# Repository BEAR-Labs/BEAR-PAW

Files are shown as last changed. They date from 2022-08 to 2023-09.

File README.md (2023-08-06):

# BEAR-PAW
                                                                                                                                                                      

Contact Information:

Email: ucdbearlabs@gmail.com

The Bionic Engineering and Assistive Robotics Pediatric Assistive Ware (BEAR PAW) is a dexterous pediatric prosthetic hand sized for the 8-year-old population and capable of multiple hand grasp configurations. The BEAR PAW has 6 degrees of actuation (individual digit flexion and thumb palmar abduction) and is an underactuated hand with 11 degrees of freedom. The figure below give a general overview of the BEAR PAW.

BEAR PAW

# License

The hardware of the BEAR PAW is released under the Creative Commons BY-SA 4.0 license. The software of the BEAR PAW is released under the GNU General Public License v3. Both licenses have local copies available in the repository under the hardware and software folders.

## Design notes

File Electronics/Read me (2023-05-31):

This is a zipped file for the PCB breakout board. Download the zipped file and then upload the zipped file to osh park (a pcb fabrication company). Use the link below.

https://oshpark.com/

Minimum order of 3 boards is required, this is perfect as you will need 1 for each hand (and an extra for potential mistakes). Should cost around $4.50 for all three.

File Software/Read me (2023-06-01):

To upload the adruino code to the Arduino Pro Mini you will need to use the FTDI USB to TTL converter. This will require that you download the FTDI drivers. Link can be found below. 

https://ftdichip.com/drivers/d2xx-drivers/

The driver version used was the 2.12.28 but this is no longer supported. It can be found at the link above but newer version should still work.

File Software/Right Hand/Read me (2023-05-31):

This is the arduino code for the right hand BEAR PAW.

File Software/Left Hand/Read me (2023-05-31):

This is the arduino code for the left hand BEAR PAW.

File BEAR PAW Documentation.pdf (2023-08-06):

### Contributors: Marcus Battraw, Martin Croshaw, Pranav Tirumalai

### Date: 8-05-23

# BEAR PAW

## Assembly Manual

## Contents

1. Introduction | 2
2. Nomenclature | 2
2.1 Digits & Joints | 2
2.2 Naming Convention for 3D Printed Parts | 3
3. Required Materials | 4
3.1 3D Printed Parts | 4
3.1.1 Table 1: Parts for 3D Printing | 4
3.2 Ordered Parts | 5
3.3 Tools | 8
4. Assembly Flowchart | 7
5. Fingers (D2|5) | 7
5.1 Preparations | 7
5.1.1 Sanding Parts in Order to Ensure Proper Fit | 7
5.1.2 Fingertip Mold | 8
5.1.3 Proximal Part (D2|5) | 8
5.1.4 Distal Part | 9
5.2 Assembly | 11
6. Thumb (D1) | 12
6.1 Preparations | 12
6.1.1 Sanding Parts in Order to Ensure Proper Fit | 12
6.1.2 Thumb-tip Mold | 13
6.1.3 Proximal Part | 13
6.1.4 Distal Part | 13
6.2 Assembly | 15
7. Palm | 17
7.1 Preparations | 17
8.2 Mount the Digits D1|5 to the Palm | 19
7.3 Motor Placement | 20
7.3.1 Wire Cutting | 20
7.4. Mounting Tendons and Motors | 22
7.4.1 Fingers - D2|5 | 22
7.4.2 Thumb - D1 | 23
7.5 Covers and Wrist | 24
8. Hardware and Software | 26
8.1 Soldering | 26
8.2 Wiring | 28
8.2 Programming | 30

## 1. Introduction

While pediatric prosthetic devices are emerging on clinical and experimental horizons, researchers are missing a well-validated, robust device with open access to hardware and software. The straightforward and inexpensive Pediatric Assistive Ware designed at the UC Davis Bionic Engineering and Assistive Robotics Lab (BEAR PAW) provides an open-source platform to bridge this gap in knowledge. Dexterous, multiarticulate, and versatile in hand grasping patterns, the BEAR PAW will provide a platform for studies to improve understanding of how children will control prostheses. Ultimately, enabling such studies will improve the translation of dexterous multi-grasp prosthetic devices to the pediatric population. Complete with materials, definitions, and pictorial instructions, this guide allows any interested individual or team to create the BEAR PAW.

## 2. Nomenclature

### 2.1 Digits & Joints

Naming convention: Digit-Position/Joint
i.e. D3-JI (Digit 3 – Intermediate Joint) or D2-DI (Digit 2 – Distal and Intermediate)
Note that “I” is for Intermediate (i.e., the joint or phalanx in the middle of the finger, but since we couple the intermediate and distal components it is also the most distal component) and “P” for proximal (i.e., the joint or phalanx attaching the finger to the palm). The ability to rotate 90° into the page (assume palm down) is an additional degree of freedom provided to the thumb, and this joint is called out as D1-R.

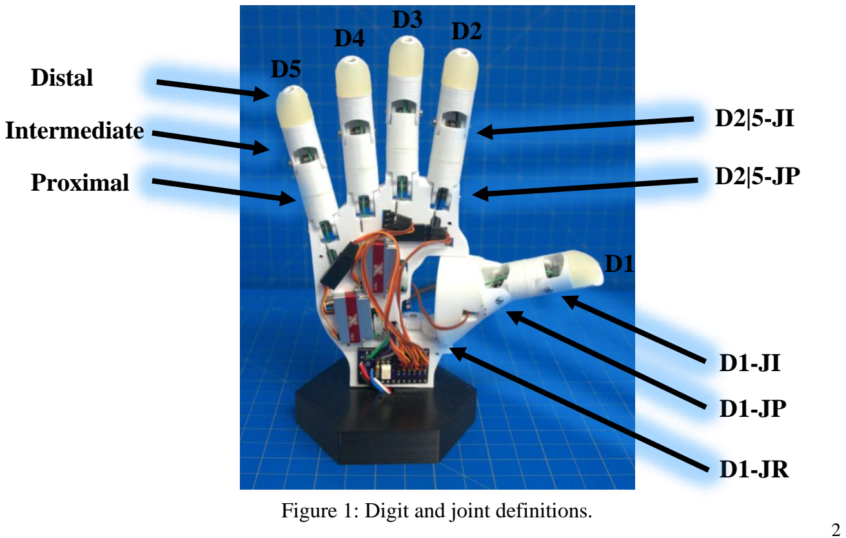
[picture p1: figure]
Figure 1: Digit and joint definitions.; Distal; Intermediate; Proximal

NOTE: The distal joint in a child’s hand poses a manufacturing obstacle due to its small nature. Additionally, it has a negligible range of motion. Thus, this design includes only two joints in each finger: the intermediate and proximal, with the distal and intermediate phalanges connected as a single part.

### 2.2 Naming Convention for 3D Printed Parts

3D-Printed Parts Code: Hand-Digit(s)/Palm-Part

Hand: Right (R), Left (L)

Digit(s): D1-D5. Since the parts and assemblies of D2, D3, D4 & D5 are identical, these are collectively called out as D2|5.

Palm: Surface of the hand.

Part: The parts for each of the above designations.

- Digit Parts: D2-D5
- Distal: (DPhal)
- Intermediate: (IPhal)
- Proximal: Comes in two parts, a distal and proximal part, for ease of printing.
- Distal-most part of proximal: (PPhal-DPart)
- Proximal-most part of proximal: (PPhal-PPart)
- Tendon tightening mount: (Tensioner)
- Negative of fingertip: Comes in two parts for easy removal of cured resin.
- (FTNeg1) and (FTNeg2)
- Thumb Parts: D1
- Distal: Comes in two parts—a distal and proximal part, for ease of printing.
- Distal-most part of distal: (DPhal-DPart)
- Proximal-most part of distal: (DPhal-PPart)
- Intermediate: Comes in two parts—a distal and proximal part, for ease of printing.
- Distal-most part of intermediate: (IPhal-DPart)
- Proximal-most part of intermediate: (IPhal-PPart)
- Proximal: Comes in five parts—for ease of printing.
- Distal-most part of proximal: (PPhal-DPart)
- Proximal-most part of proximal: (PPhal-PPart-PalmGear)
- Door, to hide motor in proximal part: (PPhal-PPart-PalmDoor)
- Gear, for motor to mesh with proximal gear for abduction: (PalmGearWheel)
- Tendon tightening mount: (Tensioner)
- Negative of fingertip: Comes in two parts for easy removal of cured resin.
- (FTNeg1) and (FTNeg2)

- Palm Parts
- Main interior frame for motor and digit mounting: (InteriorFrame)
- Front of hand cover: (PalmarCover)
- Back of hand cover: (DorsalCover)

Notes:

- Position/Location: If several parts make up a phalanx, they are referred to by location as being more proximal (closer to the palm) or distal (closer to the fingertip).
- Fingertip (FT) mold only needs to be printed once and can be reused.

## 3. Required Materials

### 3.1 3D Printed Parts

General printer settings used.

Printer | SigmaxR19
Hotend Nozzle | 0.4 mm
Material | PLA
Global Layer | 0.15 mm
Infill Density | 25%
Speed | 50 mm/s

3.1.1 Table 1: Parts for 3D Printing
Part Name | Unique Print Settings | Print Length (meters) | Approximate Print Time | Part Mass
R/L-D2|5-PPhal-PPart X 4 | None | 0.23 m X 4 = 0.92 m | 26 min X 4 = 1 hr 44 min | 2 g X 4 = 8 g
R/L-D2|5-PPhal-DPart X 4 | None | 0.21 m X 4 = 0.84 m | 24 min X 4 = 1 hr 36 min | 2 g X 4 = 8 g
R/L-D2|5-IPhal X 4 | None | 0.22 m X 4 = 0.88 m | 26 min X 4 = 1 hr 44 min | 2 g X 4 = 8 g
R/L-D2|5-DPhal X 4 | None | 0.12 m X 4 = 0.48 m | 13 min X 4 = 52 min | 1 g X 4 = 4 g
R/L-D2|5-Tensioner X 4 | None | 0.02 m X 4 = 0.08 m | 3 min X 4 = 12 min | ~ 0 g
R/L-D2|5-FTNeg1 | None | 1.00 m | 1 hr 16 min | 8 g
R/L-D2|5-FTNeg2 | None | 0.72 m | 51 min | 6 g
R/L-D1-PPhal-PPart-PalmGear | Infill 50% Global; 0.1 mm; Using Supports Advisable | 1.33 m | 2 hrs 50 min | 11 g
R/L-D1-PPhal-PPart-PalmDoor | None | 0.34m | 34 min | 3g
R/L-D1-PPhal-DPart | None | 0.29m | 28 min | 2 g

R/L-D1-IPhal-PPart | None | 0.24 m | 25 min | 2 g
R/L-D1-IPhal-DPart | None | 0.21 m | 20 min | 2 g
R/L-D1-DPhal-PPart | None | 0.15 m | 20 min | 1 g
R/L-D1-DPhal-DPart | None | 0.15 m | 15 min | 1 g
R/L-D1-PalmGearWheel | None | 0.08 m | 11 min | 1 g
R/L-D1-Tensioner | None | 0.02 m | 3 min | ~ 0 g
R/L-D1-FTNeg1 | None | 0.98 m | 1 hr 17 min | 8 g
R/L-D1-FTNeg2 | None | 0.72 m | 53 min | 6 g
R/L-Palm-DorsalCover | Infill 35% Global; 0.12 mm; Use Supports | 2.63 m | 4 hrs 53 min | 21 g
R/L-Palm-InteriorFrame | Infill 35% Global; 0.1 mm; Use Supports | 2.75 m | 6 hrs 39 min | 22 g
R/L-Palm-PalmarCover | 0.12 mm; Use Supports | 1.67 m | 3 hrs 10 min | 13 g
R/L-Wrist-BaseMount | None | 2.56 m | 3 hrs 27 min | 20 g
R/L-Wrist-HandAdapter | None | 1.22 m | 1 hr 44 min | 10 g
R/L-Wrist-HandMount | None | 1.02 m | 1 hr 27 min | 8 g
| Totals: | 21.28 m | 37 hrs 11 min | 173 g
NOTE: Supports advised when there is an extensive hole or overhanging arch; alternatively, consider printing in a different orientation.

NOTE: X 4 on the finger part values to account for all fingers D2|5.

NOTE: Printed several parts in 1 G-code file to speed up the process.

### 3.2 Ordered Parts

Table 2 below contains all the necessary items to build a complete BEAR PAW. This table was finalized on 8/25/2022; therefore, some items may be discontinued, or cost of items may have changed. The cost shown does not account for shipping/tax or any additional costs that may be incurred.

Table 2: Parts for Ordering

Item | Description | Vendor | Part
No.
Link | Qty. | Cost/Item | Ext.
Cost
SENSORS/ELECTRONICS
KST X08N V5.0 | Micro Servo Motor with no mounting flanges | Alofthobbies | X08N | https://alofthobbies.com/k st-x08n.html (https://alofthobbies.com/kst-x08n.html) | 1 | $46.00 | $46.00
KST X08H V5.0 | Micro Servo Motor with top mounting flanges | Alofthobbies | X08H | https://alofthobbies.com/k st-x08h-servo-2-8kg-38-oz-in-09-sec-8-grams-wide-voltage.html (https://alofthobbies.com/kst-x08h-servo-2-8kg-38-oz-in-09-sec-8-grams-wide-voltage.html) | 1 | $46.00 | $46.00
KST X08 V5.0 | Micro Servo Motor with side mounting flanges | Alofthobbies | X08 | https://alofthobbies.com/k st-x08-servo-2-8kg-38-oz-in-09-sec-8-grams.html (https://alofthobbies.com/kst-x08-servo-2-8kg-38-oz-in-09-sec-8-grams.html) | 4 | $46.00 | $184.00
Breakout Board | 2 layer electronics breakout board, 17.8 x 33.0mm | OSHPARK | Find Gerber files on GitHub | https://docs.oshpark.com/services/two-layer/ (https://docs.oshpark.com/services/two-layer/) | 1 | $5.00 | $5.00
Solid State Relay | Omron, Solid State Relay - PCB Mount, 3 A, 60 V | Mouser Electronics | 653-G3VM-61AR1 | https://www.mouser.com/ProductDetail/Omron-Electronics/G3VM-61AR1?qs=wnTfsH77Xs7 4FCx6Uqk9GQ%3D%3D (https://www.mouser.com/ProductDetail/Omron-Electronics/G3VM-61AR1?qs=wnTfsH77Xs74FCx6Uqk9GQ%3D%3D) | 1 | $6.91 | $6.91
Resistor | 5,600 Ohm Resistor, 5%, 0.5W Through Hole Resistor | DigiKey | S5.6KH CT-ND | https://www.digikey.com/en/products/detail/stackpol e-electronics-inc/CFM12JT5K60/17419 74?s=N4IgTCBcDaIMID ECyBGMApAKgVgNID YAGEAXQF8g (https://www.digikey.com/en/products/detail/stackpole-electronics-inc/CFM12JT5K60/1741974?s=N4IgTCBcDaIMIDECyBGMApAKgVgNIDYAGEAXQF8g) | 1 | $0.10 | $0.10
Arduino Pro Mini 238 – 3.3V/ 8MHz | Micro Controller | Sparkfun | DEV-11114 | https://www.sparkfun.com/products/11114 (https://www.sparkfun.com/products/11114) | 1 | $10.95 | $10.95
FTDI Mini USB to TTL | Mini USB to TTL Adapter Board for Arduino | Amazon | B00IJXZ Q7C | https://www.amazon.com/HiLetgo-FT232RL-Converter-Adapter-Breakout/dp/B00IJXZQ7C/ (https://www.amazon.com/HiLetgo-FT232RL-Converter-Adapter-Breakout/dp/B00IJXZQ7C/) | 1 | $6.99 | $6.99
Bluetooth Module | DSD Tech HC-05 Bluetooth Serial Module | Amazon | B01G9K SAF6 | https://www.amazon.com/DSD-TECH-HC-05-Pass-through-Communication/dp/B01G9KSAF6/ (https://www.amazon.com/DSD-TECH-HC-05-Pass-through-Communication/dp/B01G9KSAF6/) | 1 | $9.99 | $9.99
Power Wires | 22 Gauge Silicone wire spool red 25ft and black 25ft | Amazon | B07HGT 44XY | https://www.amazon.com/BNTECHGO-Silicone-Flexible-Strands- (https://www.amazon.com/BNTECHGO-Silicone-Flexible-Strands-Stranded/dp/B07HGT44XY/?th=1) | 1 | $9.98 | $9.98

| | | | Stranded/dp/B07HGT44X Y/?th=1 (https://www.amazon.com/BNTECHGO-Silicone-Flexible-Strands-Stranded/dp/B07HGT44XY/?th=1)
Extra Servo Wires | 30 Gauge Silicone Wire Kit | Amazon | B01M70 EDCW | https://www.amazon.com/dp/B01M70EDCW?th=1 (https://www.amazon.com/dp/B01M70EDCW?th=1) | 1 | $9.98 | $9.98
Connecto r Kit | 2.54 mm Crimp Pin Connector Housings, Single Row Male Headers, Male/Female Crimp Pins and Ribbon Cable | Amazon | B078RR PRQZ | https://www.amazon.com/Dupont-Connector-Kit-Connectors-Plusivo/dp/B078RRPRQZ/ (https://www.amazon.com/Dupont-Connector-Kit-Connectors-Plusivo/dp/B078RRPRQZ/) | 1 | $12.99 | $12.99
Wall Adapter | AC/DC Wall Mount Adapter 5V, 20W | DigiKey | 102-4196-ND | https://www.digikey.ca/en/products/detail/cui-inc/SWI25-5-N-P5/7070092 (https://www.digikey.ca/en/products/detail/cui-inc/SWI25-5-N-P5/7070092) | 2 | $27.89 | $55.78
Wall Jack | DC Barrel Jack Adapter - Female | Sparkfun | 10288 | https://www.sparkfun.com/products/10288 (https://www.sparkfun.com/products/10288) | 2 | $3.50 | $7.00
CENTAU RUS Servo Tester STV2.3 | Steering Gear Rudder Detector Spare Parts for RC Aircraft Micro FPV DC 4.8V-6V | Amazon | B09LXT W19G | https://www.amazon.com/CENTAURUS-Steering-Detector-Aircraft-4-8V-6V/dp/B09LXTW19G (https://www.amazon.com/CENTAURUS-Steering-Detector-Aircraft-4-8V-6V/dp/B09LXTW19G) | 1 | $3.50 | $3.50

HARDWARE AND MISCELLANOUS
Bearings | Bearing 2 mm Bore ID, 5 mm OD, 2.5mm | Amazon | B07X9T 5F81 | https://www.amazon.com/Donepart-MR52ZZ-Bearings-Miniature-Equipment/dp/B07X9T5F 81 (https://www.amazon.com/Donepart-MR52ZZ-Bearings-Miniature-Equipment/dp/B07X9T5F81) | 1 | $9.99 | $9.99
Pulley for KST X08 Servo | Pulley for KST Servo Pack of 4 | Hyperflight | X08-PULLE Y | https://www.hyperflight.co.uk/products.asp?code=X 08-PULLEY&name=pulley-for-kst-x08-servos-4 (https://www.hyperflight.co.uk/products.asp?code=X08-PULLEY&name=pulley-for-kst-x08-servos-4) | 2 | $11.75 | $23.50
Rotary Shaft 316 Stainless Steel | 2 mm Shaft 200 mm long | McMaster Carr | 1265K17 | https://www.mcmaster.com/1265K17/ (https://www.mcmaster.com/1265K17/) | 1 | $14.27 | $14.27
Torsion Spring | Torsion Spring 180 Degree Right-Hand Wound, 0.186'' OD (Pack of 6) | McMaster Carr | 9271K66 5 | https://www.mcmaster.com/9271K665/ (https://www.mcmaster.com/9271K665/) | 2 | $5.19 | $10.38
Strength Black Synthetic Cable | 0.75mm (0.03") in diameter, 5 m long, 45kg strength | ServoCity | 2908-0075-0005 | https://www.servocity.com/synthetic-cable-black-0-75mm-diameter-5m-length/ (https://www.servocity.com/synthetic-cable-black-0-75mm-diameter-5m-length/) | 1 | $2.99 | $2.99

M2 18-8 Stainless Steel Screw | Narrow Cheese Head Slotted Screws M2 x 0.4mm Thread, 25 mm Long (50 Pack) | McMaster Carr | 91800A0 23 | https://www.mcmaster.com/91800A023/ (https://www.mcmaster.com/91800A023/) | 1 | $10.15 | $10.15
M3 18-8 Stainless Steel Pan Head Screw | M3 x 0.5mm Thread, 8m m Long | McMaster Carr | 92000A1 18 | https://www.mcmaster.com/92000A118/ (https://www.mcmaster.com/92000A118/) | 1 | $5.51 | $5.51
#4 x 1/2" Flat Head Sheet Metal Screws | Screws for attaching the hand onto the wrist mount | Amazon | B08L23 164W | https://www.amazon.com/Sheet-Screws-Phillips-Tapping-Stainless/dp/B08L23164W/ (https://www.amazon.com/Sheet-Screws-Phillips-Tapping-Stainless/dp/B08L23164W/) | 1 | $9.49 | $9.49

Heat Shrink Tubing Kit | Heat Shrink Tubing (650 pcs) | Amazon | B07QM 8249H | https://www.amazon.com/625pcs-Shrink-Tubing-Tubes-Ratio/dp/B07QM8249H/ (https://www.amazon.com/625pcs-Shrink-Tubing-Tubes-Ratio/dp/B07QM8249H/) | 1 | $8.79 | $8.79
Textured Rubber | Multipurpose Neoprene with Crisscross Texture Adhesive-Back Sheet, 12" x 12", 1/32" Thick | McMaster Carr | 8445K61 | https://www.mcmaster.com/8445K61/ (https://www.mcmaster.com/8445K61/) | 1 | $16.67 | $16.67

MATERIALS
Smooth-On Dragon Skin | 10 NV, 2 Pint Set, Trial Unit 2lbs (Moldable material for fingertips) | Reynolds Advanced Materials | MC-1244 | https://www.reynoldsam.com/product/dragon-skin/ (https://www.reynoldsam.com/product/dragon-skin/) | 1 | $35.37 | $35.37
Gorilla Super Glue Gel XL | 25 grams, clear | Amazon | B082XG L21J | https://www.amazon.com/Gorilla-Super-Glue-transparente-102433/dp/B082XGL21J/ (https://www.amazon.com/Gorilla-Super-Glue-transparente-102433/dp/B082XGL21J/) | 1 | $8.88 | $8.88
| | | | | | Total | $571.16

### 3.3 Tools

- SigmaX R19 (3D Printer)
- Crimping Tool

(https://www.amazon.com/dp/B087BGTH1Y)
- Sandpaper / Sanding Tool (Dremel)
- Screwdriver
- Wire Strippers
- Wire Cutter
- Tweezers
- Pliers
- Files
- Soldering Iron & Solder
- Knife
- Heat Gun

## 4. Assembly Flowchart

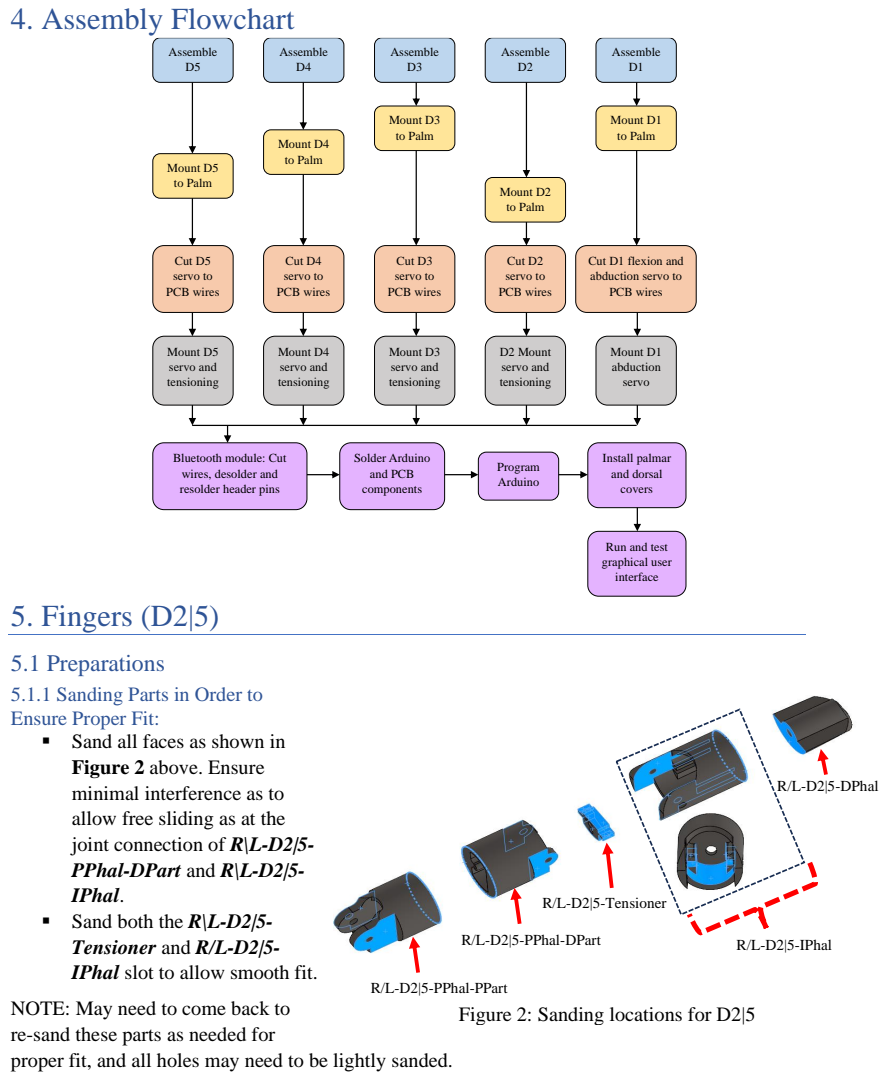
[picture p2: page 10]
5. Fingers (D2|5); R/L-D2|5-PPhal-PPart; R/L-D2|5-PPhal-DPart; R/L-D2|5-Tensioner; R/L-D2|5-IPhal; R/L-D2|5-DPhal; Assemble D5; Assemble D4; Assemble D3; Assemble D2; Assemble D1; Mount D5 to Palm; Mount D4 to Palm; Mount D3 to Palm; Mount D2 to Palm; Mount D1 to Palm; Mount D5 servo and tensioning; Mount D3 servo and tensioning; Mount D4 servo and tensioning; D2 Mount servo and tensioning; Mount D1 abduction servo; Cut D5 servo to PCB wires; Cut D4 servo to PCB wires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

Cut D1 flexion and
abduction servo to
PCB wires

Bluetooth module: Cut
wires, desolder and
resolder header pins

Run and test
graphical user
interface

5.1 Preparations
5.1.1 Sanding Parts in Order to
Ensure Proper Fit:
▪ Sand all faces as shown in
Figure 2 above. Ensure
minimal interference as to
allow free sliding as at the
joint connection of R\L-D2|5-
PPhal-DPart and R\L-D2|5-
IPhal.
▪ Sand both the R\L-D2|5-
Tensioner and R/L-D2|5-
IPhal slot to allow smooth fit.

NOTE: May need to come back to
re-sand these parts as needed for
proper fit, and all holes may need to be lightly sanded.

Figure 2: Sanding locations for D2|5

5.1.2 Fingertip Mold
1. After the R/L-D2|5-FTNeg1 and R/L-D2|5-FTNeg2 are printed, slot together if possible or file to fit in.
2. Then, mix equal parts A and B of the Smooth-On Dragon Skin and pour into the mold. Wait for the recommended time suggested by the Smooth-On instructions.
3. If excess Smooth-On is at the top, cut off evenly with an X-Acto knife.
4. Afterwards, pull apart the mold and repeat the process over again until you have 4 fingertips (Figure 3).

Figure 3: Negative molds for fingertips and thumb

5.1.3 Proximal Part (D2|5)
Orient the two proximal pieces as shown in Figure 4 and glue them.

Proximal torsion spring slots may need to be cleaned so that the spring leg fits in.

This may be difficult even with a small file.

Suggestion: use gloves and a soldering iron. Heat up the spring leg and press the hot leg through the hole to clean it out. Remove before the plastic solidifies.

Rubber

FTNeg
FTNeg
Towards distal end | Distal torsion spring slot

5.1.4 Distal Part
Glue the R/L-D2|5-IPhal to the R/L-D2|5-DPhal; then glue the rubber fingertip on last. See Figures 5a and 5b.

NOTE: It is
convenient to
screw in the
25mm string
tensioner
screw when
gluing these
parts as it
helps keep
everything
aligned.
A. Tendon preparation (D2-5)
1. Prepare the tendon string (synthetic cable) by cutting a 150mm piece. The actual functional length of the string—once completed and assembled—is only about 60mm, but excess allows for error to be corrected. Cut this length of string, careful to do so with as little fraying as possible.
2. Use the M2X25 tensioner screw and screw into the distal part for the string tensioner (Figure 6).
3. The hole for the torsion spring may be difficult to clean even with a small file. Suggestion: use gloves and a soldering iron. Heat up the spring leg and press the hot leg through the hole to clean it out. Remove before the plastic solidifies (Figure 6).
4. Insert the tendon string through to the distal-facing side of the string tensioner and tie a simple knot to secure (knot should be on the side that points towards the fingertip). Remove any excess string.

Figure 5b: Gluing distal surfaces for D2|5

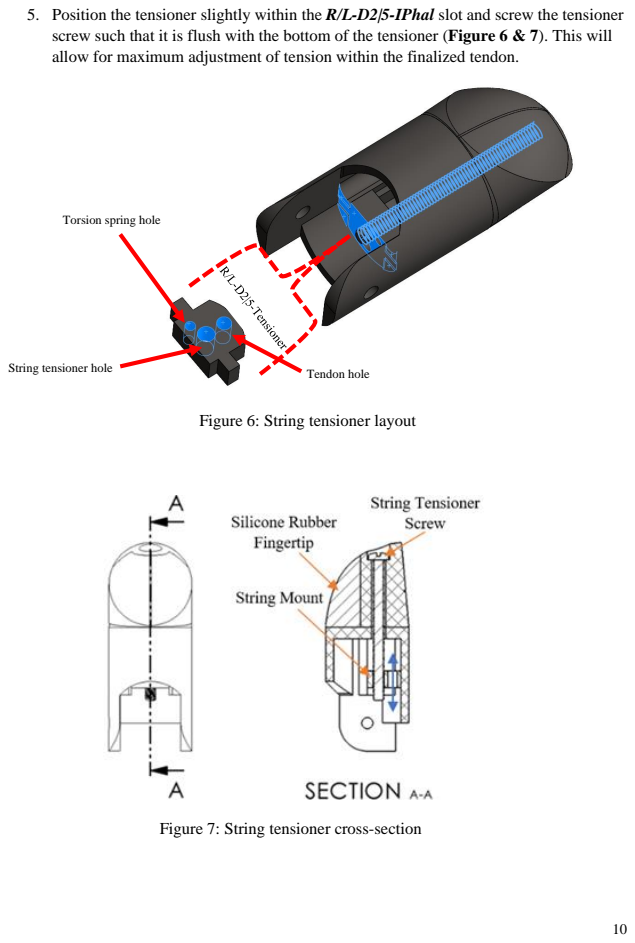
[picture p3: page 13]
Tendon hole

5. Position the tensioner slightly within the R/L-D2|5-IPhal slot and screw the tensioner
screw such that it is flush with the bottom of the tensioner (Figure 6 & 7). This will
allow for maximum adjustment of tension within the finalized tendon.

Torsion spring hole

String tensioner hole

Figure 6: String tensioner layout

Figure 7: String tensioner cross-section

### 5.2 Assembly

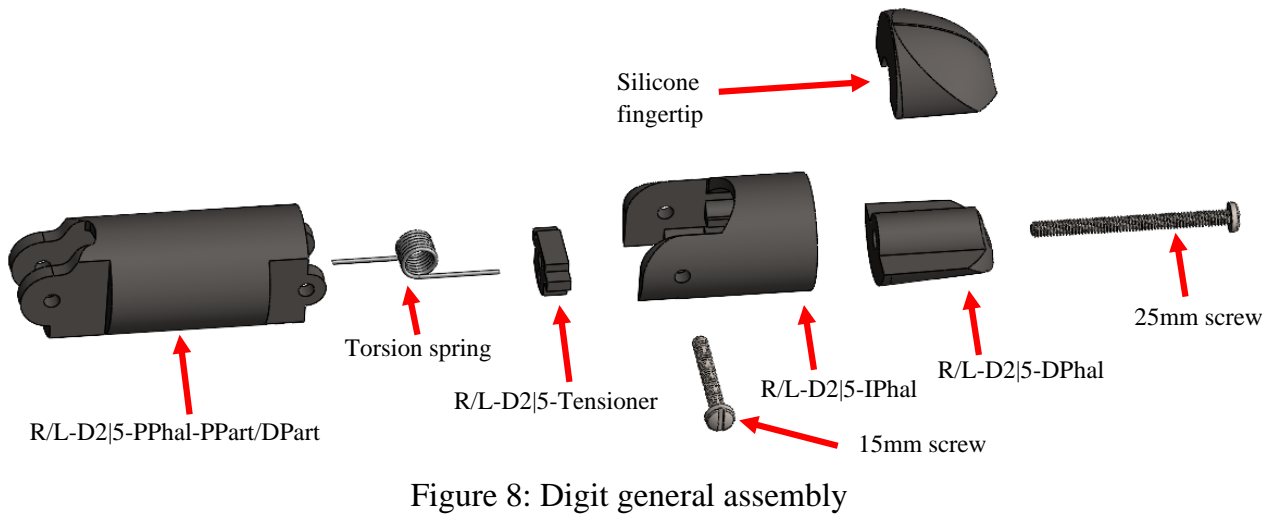
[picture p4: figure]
Figure 8: Digit general assembly; Silicone fingertip; R/L-D2|5-PPhal-PPart/DPart; Torsion spring; R/L-D2|5-Tensioner; R/L-D2|5-IPhal; R/L-D2|5-DPhal; 15mm screw; 25mm screw

1. Cut the screws for joints D2|5-JI and D2|5-JP (15mm). The screw for D2|5-JP will be used later for assembling the digits to the palm.
2. Cut spring legs (they should be approximately 13mm) for joints D2|5-JI.
3. Then with the torsion spring slotted in the torsion spring hole (Figure 6) and the R/L-D2|5-IPhal distal torsion spring slot (Figure 4) join them with the 15mm screw ensuring that the screw goes through the spring and that the tendon is on the palmar side of the digit.

NOTE: Refer to Figure 8 for general layout.

NOTE: Fish the tendon through the palmar side of the finger.

## 6. Thumb (D1)

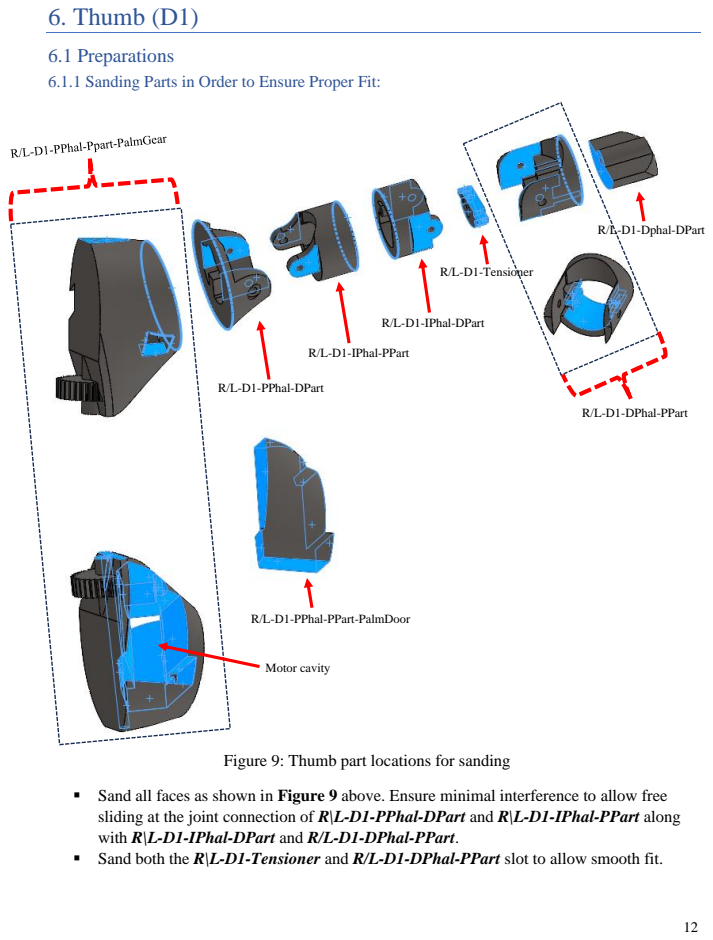
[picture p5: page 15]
R/L-D1-PPhal-DPart; R/L-D1-IPhal-PPart; R/L-D1-IPhal-DPart; R/L-D1-Tensioner; R/L-D1-DPhal-PPart; R/L-D1-Dphal-DPart; Motor cavity

6.1 Preparations
6.1.1 Sanding Parts in Order to Ensure Proper Fit:

R/L-D1-PPhal-PPart-PalmDoor

Figure 9: Thumb part locations for sanding

▪ Sand all faces as shown in Figure 9 above. Ensure minimal interference to allow free
sliding at the joint connection of R\L-D1-PPhal-DPart and R\L-D1-IPhal-PPart along
with R\L-D1-IPhal-DPart and R/L-D1-DPhal-PPart.
▪ Sand both the R\L-D1-Tensioner and R/L-D1-DPhal-PPart slot to allow smooth fit.

- Sand the D1-PPhal-PPart-PalmGear motor cavity so that the servo motor with no flanges fits inside.
- Cut the rod to 57mm. Then, sand the thumb abduction rod to
ensure that it fits into the 2mm inside diameter of the
bearings. This can be done using a hand drill and sandpaper. (See hand drill used in Figure 10 to the right.) Attach the rod as you would a drill bit and pull the trigger while you sand the rod back and forth with the sand paper. Take out the rod
and repeat again on its opposite side. Do this until the rod fits
in the bearing with some resistance.

NOTE: May need to come back to re-sand these parts as needed for proper fit.

6.1.2 Thumb-tip Mold

Refer to Figure 3, Section 5.1.2—similar mold cast for the thumb.

6.1.3 Proximal Part:
1. Ensure the hole on the flat face of the proximal piece goes all the way through to the interior motor cavity (sand if needed), as the tendon string will pass through this hole. The proper hole pathway can be seen in the SolidWorks model provided (Figure 11a).
2. Glue the two parts together in the orientation shown in Figure 11b to the right.

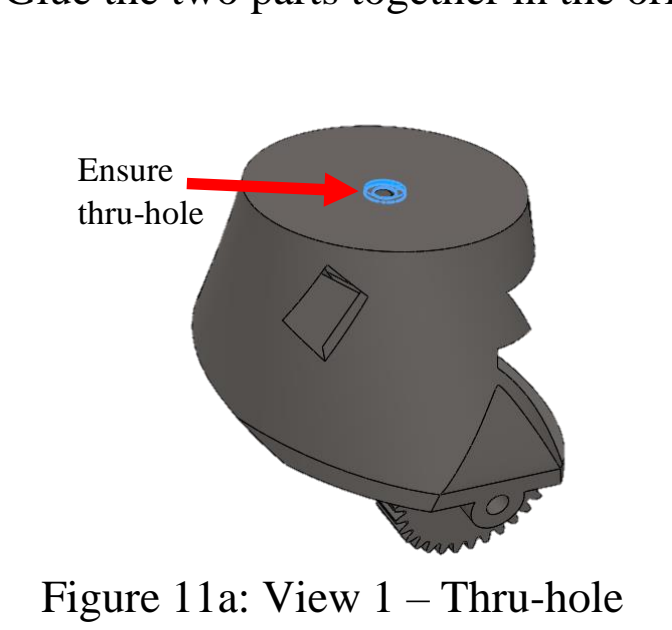
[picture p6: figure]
Figure 11a: View 1 – Thru-hole; Ensure thru-hole

6.1.4 Distal Part:

A. Glue together D1-IPhal-DPart and D1-IPhal-PPart such that the interior slots meant for the torsion springs are on opposite sides as shown in Figure 12. Complete the same process for D1-DPhal-DPart and D1-DPhal-PPart (Figure 13). Additionally, glue the rubber fingertip to the distal part.

Proximal torsion spring slots may need to be cleaned so that the spring leg fits in. This may be difficult even with a small file.

Figure 10: Hand drill used.

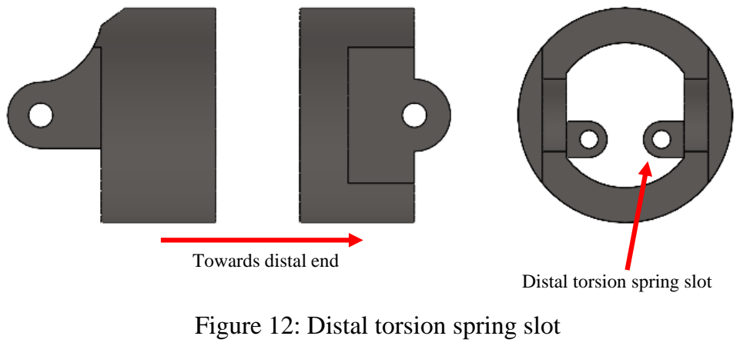
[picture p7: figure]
Distal torsion spring slot; Towards distal end; Figure 12: Distal torsion spring slot

Suggestion: Use gloves and a soldering iron. Heat up the spring leg and press the hot leg through the hole to clean it out. Remove before the plastic solidifies.

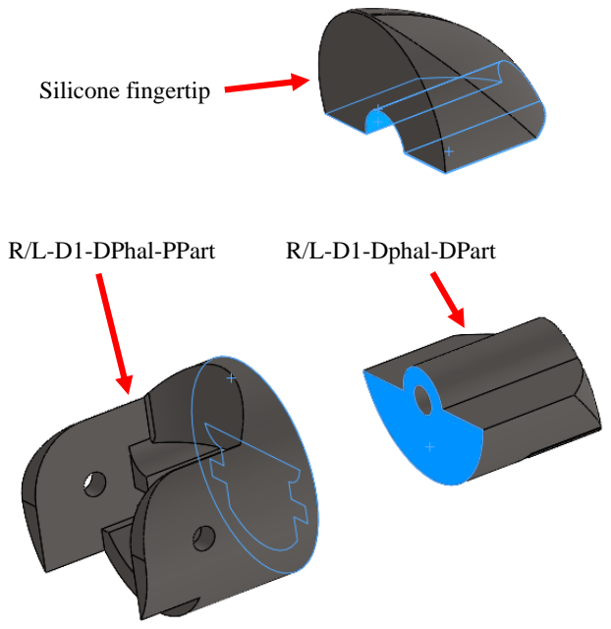
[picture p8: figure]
R/L-D1-DPhal-PPart; R/L-D1-Dphal-DPart; Silicone fingertip

B. Tendon preparation (D2-5)
1. Prepare the tendon string (synthetic cable) by cutting a 150mm piece. The actual functional length of the string once completed and assembled is only about 60mm, but excess allows for error to be corrected. Cut this length of string, careful to do so with as little fraying as possible.
2. Pass the tendon through the D1-PPhal-PPart-PalmGear through-hole as seen in Figure 11a (should be sticking through on both sides).
3. Use the servo motor with no mounting flanges and zero it out with the servo tester (make sure that the zero position is correct such that when the servo is in the thumb it will wind the tendon in the correct direction to flex the thumb). The motor will be installed inside the D1-PPhal-PPart-PalmGear with the pulley side going in first.

Figure 13: Gluing distal surfaces for thumb

4. Using a pointed-nose file, expand the slotting hole (Figure 14) such that the tendon string can pass through with little fraying and resistance. Take care not to completely file away the exterior wall of the slotting hole. Filing of the surrounding features of the pulley may be necessary.
5. Using a lighter or heat gun, burn the 10-15mm of excess string to reduce length, ensuring it sticks to the pulley.
6. Mount the pulley to the servo arm with the servo screw.
7. Place the servo motor inside the D1-PPhal-PPart-PalmGear motor cavity with the pulley side in first. Ensure that the servo wire goes through the slot on the back side.
8. Pull the tendon through the top lightly making sure not to rotate the servo motor. If so, re-zero with the servo tester.

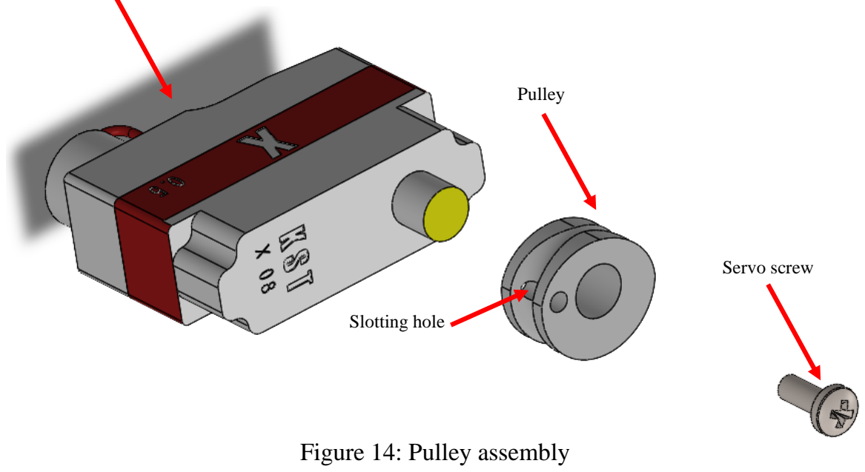
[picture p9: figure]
Pulley; Servo screw; Figure 14: Pulley assembly; Slotting hole

### 6.2 Assembly

1. Cut and file the end of three M2X25 screws; one should be 21mm (proximal joint) D1-JP, the other two should be 18mm (distal joint D1-JI and tensioner screw).
2. At this point, the proximal, intermediate, and distal parts should be completed, along with a string/tendon attached to the installed servo motor and coming out of the thru-hole on part D1-PPhal-PPart-PalmGear.
3. Cut and bend the torsion spring legs so that they fit in the R/L-D1-PPhal-DPart spring slot (90°) and the R/L-D1-IPhal-PPart spring slot. Then use the 21mm screw to attach these two parts while ensuring the screw goes through the center of the torsion spring.
4. Use the 18mm tensioner screw and screw into the now-assembled distal thumb for the string tensioner.

Servo motor

5. Fish the tendon through the glued intermediate part (R/L-D1-IPhal-PPart/DPart) ensuring it is on the palmar side of the spring. Insert the tendon string through to the proximal-facing side of the R/L-D1-Tensioner.
6. (This is the difficult part.) Move the distal thumb assembly of the thumb into position as if you were going to attach it. Observe the length of the tendon needed such that the tensioner can reach the tensioner slot. Remember to provide an extra 2-3mm to the string/tendon as it will have to go over the spring once it is fully assembled. Now tie a simple knot to secure the string/tendon, and place the tensioner in the R/L-D1-DPhal-PPart tensioner slot of the distal thumb assembly. Finally, screw the tensioner screw just enough to grab the tensioner.
7. Now cut the torsion spring legs (approximately 13mm) for D1-JI and place within slots of R/L-D1-IPhal-DPart spring hole and R/L-D1-Tensioner spring hole (remember the tendon should be on the palmar side of the spring). Now join these two parts with the second 18mm screw ensuring it goes through the torsion spring center.
8. Zero out the motor again because it may move during this process. Check to see if the tendon is too loose. You can tighten the tensioner screw, but it may be very loose even after tightening. At this point, you may have to remove the screw at D1-JI and make the string a little shorter (reassemble and try again).
NOTE: This process may take some time, be very careful you don’t rush it or you will remove too much string!

NOTE: Refer to Figure 15 below for general layout.

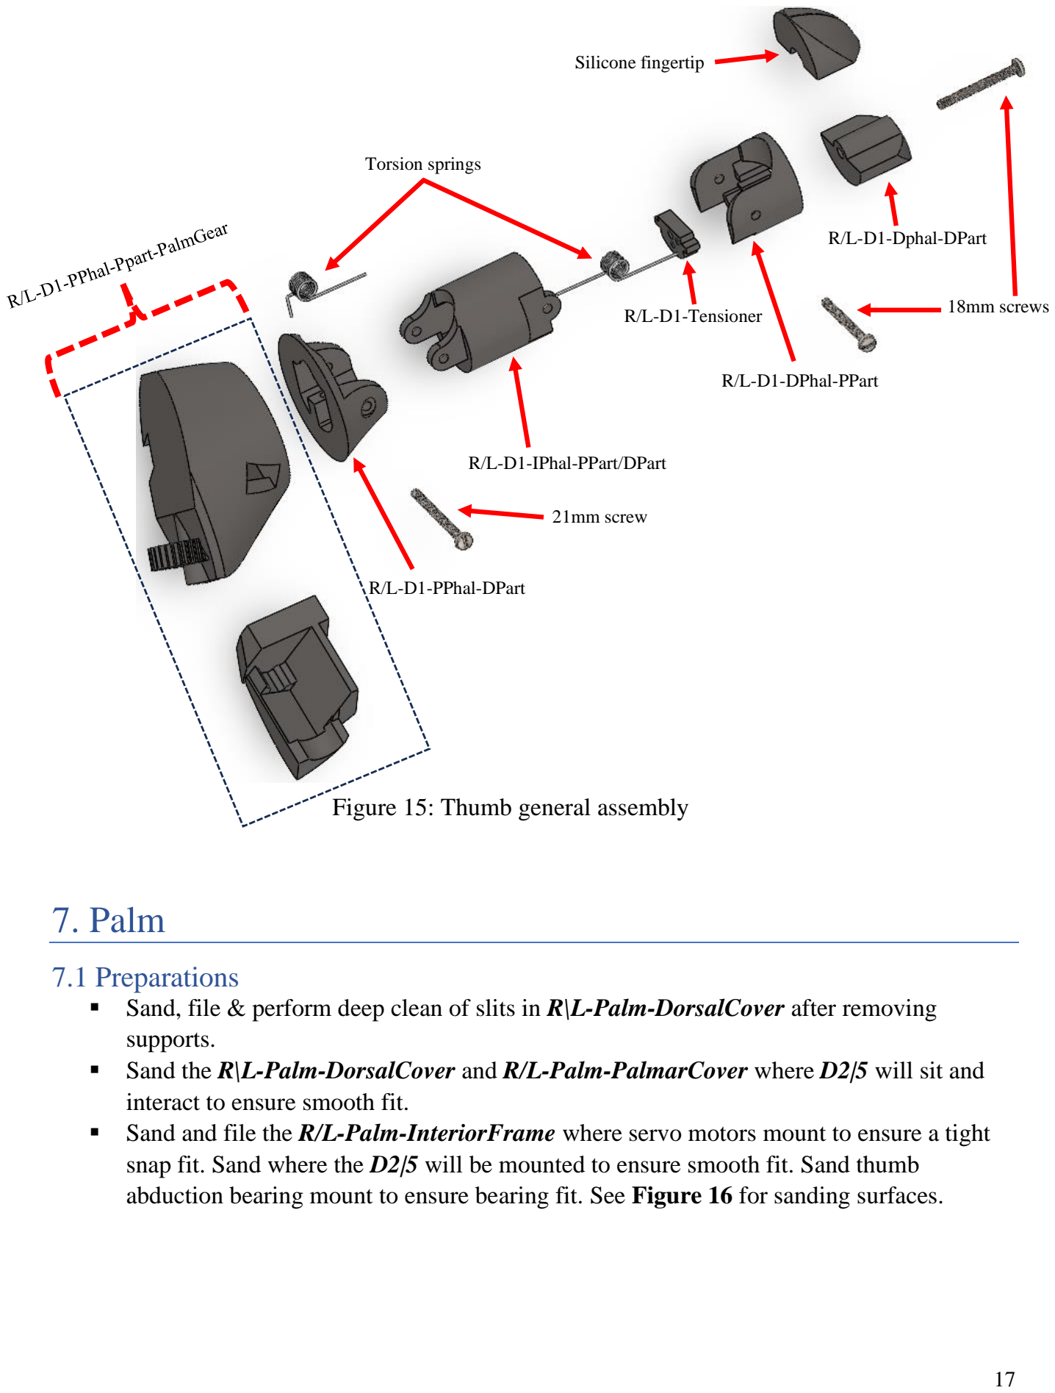
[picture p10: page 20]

## 7. Palm

### 7.1 Preparations

- Sand, file & perform deep clean of slits in R\L-Palm-DorsalCover after removing supports.
- Sand the R\L-Palm-DorsalCover and R/L-Palm-PalmarCover where D2|5 will sit and interact to ensure smooth fit.
- Sand and file the R/L-Palm-InteriorFrame where servo motors mount to ensure a tight snap fit. Sand where the D2|5 will be mounted to ensure smooth fit. Sand thumb abduction bearing mount to ensure bearing fit. See Figure 16 for sanding surfaces.

R/L-D1-PPhal-DPart

R/L-D1-IPhal-PPart/DPart

R/L-D1-DPhal-PPart

R/L-D1-Dphal-DPart

Silicone fingertip

R/L-D1-Tensioner

Torsion springs

21mm screw

18mm screws

Figure 15: Thumb general assembly

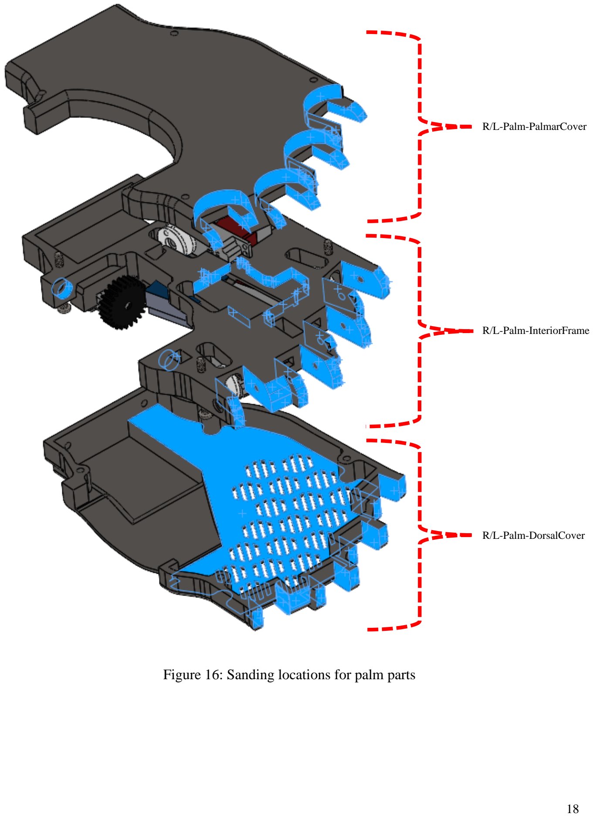
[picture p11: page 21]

R/L-Palm-PalmarCover

R/L-Palm-InteriorFrame

R/L-Palm-DorsalCover

Figure 16: Sanding locations for palm parts

- Insert bearings into R/L-Palm-InteriorFrame as shown in Figure 17.

### 8.2 Mount the Digits D1|5 to the Palm

1. General digit attachment to palm can be seen in Figure 18.
2. Cut the torsion springs for D2|5-JP. The leg that goes up into the proximal R/L-D2|5-PPhal-PPart will need to be trimmed to approximately 13mm.
3. Assemble the digits in the following order: D3, D4, D5, D2.
4. Place the torsion spring up in the given digit spring slot. Make sure the tendon is on the palmar side of the spring. Put the digit in place with the other end of the torsion spring pressing against the palm. Screw in the 15mm D2|5-JP screw that was cut earlier in the digit assembly section.
5. The leg of the torsion spring that presses against the palm will
need to be cut short and pressed into the palm by heating with a
soldering iron. (See figure to the right.)
6. Repeat steps 3 and 4 until digits D2|5 are secured.
7. Now align the thumb on the palm and slot the 2mm rod through the bearings and the proximal part D1-PPhal-PPart-PalmGear.

Figure 17: Motor placement

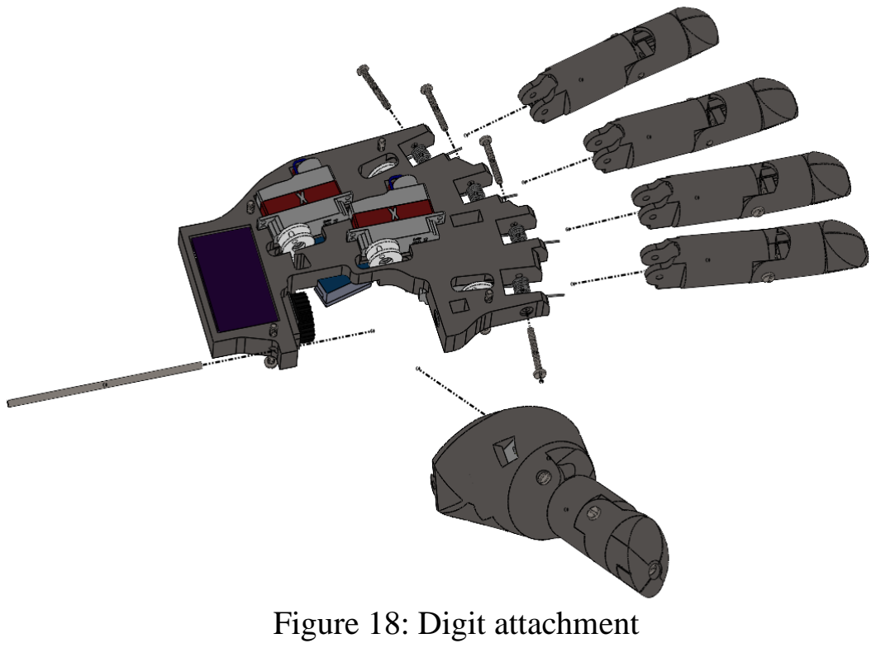
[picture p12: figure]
Figure 18: Digit attachment

### 7.3 Motor Placement

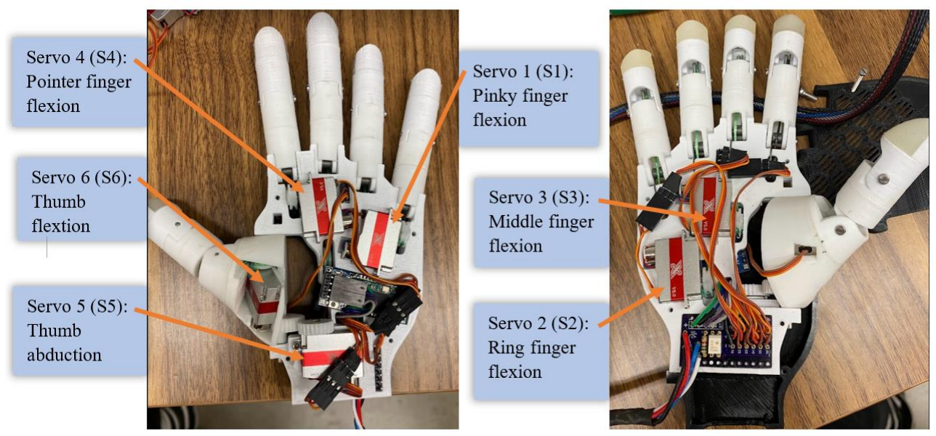
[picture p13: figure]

Servo Pin on Breakout PCB | Digit | Flange type | Wire length from motor (mm) – Female end | Wire length from PCB (mm) – Male end
(Servo 1) S1 | Pinky Flex | Vertical flange | 60 | 80
(Servo 2) S2 | Ring Flex | Vertical flange | 40 | 100
(Servo 3) S3 | Middle Flex | Vertical flange | 50 | 90
(Servo 4) S4 | Pointer Flex | Vertical flange | 80 | 60
(Servo 5) S5 | Thumb Abduction | Horizontal flange | 65 | 75
(Servo 6) S6† | Thumb Flex | No flange | 95 | 100
† There will not be enough wire left over from the servo motor (S6) after it is cut so you will need to use the Extra Servo Wires to accommodate the length from the PCB.

Each servo motor needs to be cut and have male/female ports added to the junction to allow for disconnection without disassembly. See Table 3 for servo wire cut list.

7.3.1 Wire Cutting
Wire Cut Procedure (Female End): This is the wire still attached to the servo motors.

Table 3. Servo motor number, pin on PCB, and wire cut lengths

Figure 19a: Dorsal side servo motor reference

Figure 19b: Palmar side servo motor reference

The cut list is designed to account for errors in cutting, so if done as in Table 3 above, the system will have a slight amount of slack in the final assembly.

Cut the servo wires to the appropriate length as given in Table 3.

Section below explains how to use the crimping tool.

1. Strip 2-3mm of insulation off each of the three wires to expose the proper amount of conductor. Twist conductor to prevent splaying, or “frizzing.”
2. Make sure each wire is separated 10mm to allow for ease in crimping.
3. Load a 10mm connector piece into the small end of the crimping device (https://www.amazon.com/dp/B087BGTH1Y). Make sure the larger set of wings is flush with the surface of the crimping tool.
4. Insert one servo wire such that the first set of connector wings may anchor into the insulation of the wire and the second set of wings touches the exposed conductor. Squeeze the device to the tightest setting and release.
5. Inspect the connector: lightly pull back and forth. If some movement occurs, use needlenose pliers to adjust the connection to make it more fit. Make sure the smaller wings are in good connection with the conductor.
6. Repeat connections for the remaining two wires.
7. Once all three connectors are attached, carefully insert all three connectors into a threeslot plastic housing receptacle. Make sure all connectors are top-side up (should see a small square facing up on each connector).
8. Insert connectors into housing until you hear 3 clicks, one for each wire. Repeat for each wire of every servo motor.

Wire Cut Procedure (Male End): This is the wire that will attach to the PCB.

1. Remove the existing female-adapter and connector pieces off the three wires. Do this by cutting midway along the housing unit to break the plastic and expose the connector pieces at the end of each wire. Pull the connector pieces off using the pliers, exposing the conductor.
2. Break off a set of 3 header pins using the pliers. Cut off three 10mm pieces of heat-shrink insulator and load onto each of the newly cut wire ends. Separate the wires, giving about 50mm of range between the soldering gun and the loaded heat shrink (to avoid premature shrinking).
3. Solder each wire to the shorter end of a header pin, and ensure the order of wires remains consistent (i.e., Brown-Red-Orange). Once a connection has been made between two
Figure 20a: | Figure 20b: | Figure 20c:

wires, load the heat-shrink insulator over the exposed conductor and apply a conservative amount of heat to the area (too much heat can melt the solder underneath and disrupt the connection).
4. Complete this process for male-ended wires S1-5. For wire S6, complete the same steps as listed above, however, use a set of 3 right-angled header pins.

### 7.4. Mounting Tendons and Motors

7.4.1 Fingers - D2|5
NOTE: Zero out the servo motor before attaching tendon using the servo tester. The zero direction of the servo depends on the location of the servo motor.
A. Servo pulley preparation (applicable for D2|5):
1. Attach a servo pulley to the servo arm such that the flat side of the pulley is facing away from the palm and the curved side is facing into the palm. Identify the hole in the pulley that is furthest from the distal finger joint and facing into the servo. We will call this hole the slotting hole (see Figure 21 below).
2. Take the pulley off and using a pointed-nose file, expand the slotting hole such that the tendon string can pass through with little fraying and resistance. Take care not to completely file away the exterior wall of the slotting hole. Filing of the surrounding features of the pulley may be necessary.
3. Pass the tendons through their appropriate pathways in the palm.
4. Then slot the tendon string through the slotting hole of the servo pulley such that the string passes over the pulley’s track. When the pulley is lined up to be mounted to its servo, the string should be in the gap between the pulley and the servo.
5. Pull the string through the pulley hole as it is aligned with its actual placement. To do this, you may need the servo motor in position.
6. Once the appropriate length for the tendon is determined, cut any excess leaving about 10-15mm.
7. Using a lighter or heat gun, burn the 10-15mm excess string to reduce length, ensuring it sticks to the pulley.
8. Mount the pulley to the servo arm. Using the servo tester, bend the finger. If a large amount of slack is present during the initial bend of the finger, remove the pulley and remount it in a configuration that has less slack. If a small amount of slack is present, tighten the pulley onto the servo with the servo screw and put the servo in place.
9. Then, tighten the tensioner via the flathead screw on the tip of the finger. Adjust until optimal tension is acquired, such that when using the servo tester only a small movement of the knobs starts moving the finger.

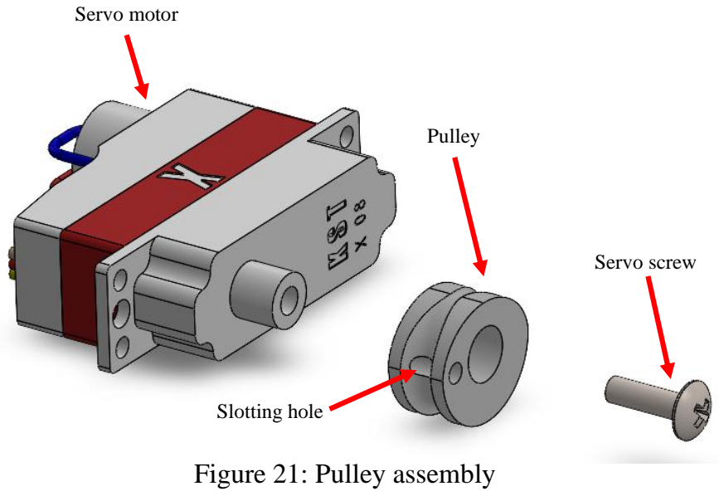
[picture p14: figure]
Servo motor; Pulley; Servo screw; Figure 21: Pulley assembly; Slotting hole

7.4.2 Thumb - D1
1. Zero out the motor for the thumb abduction (Servo 5).
2. Place the R/L-D1-PalmGearWheel on the servo and screw in.
3. Move the thumb just under parallel with the palm and place the servo with the gear into its position. If it does not go in you may need to take the 2mm rod out of the thumb to adjust. If it is too close to the R/L-D1-PPhal-PPart-PalmGear you may need to shim Servo 5. (Place a few small sheets of paper under the motor to raise it up for a good gear mesh to prevent gear binding). Screw the servo motor to its place with the screws provided with the servo motor. (See Figure 22 below.)

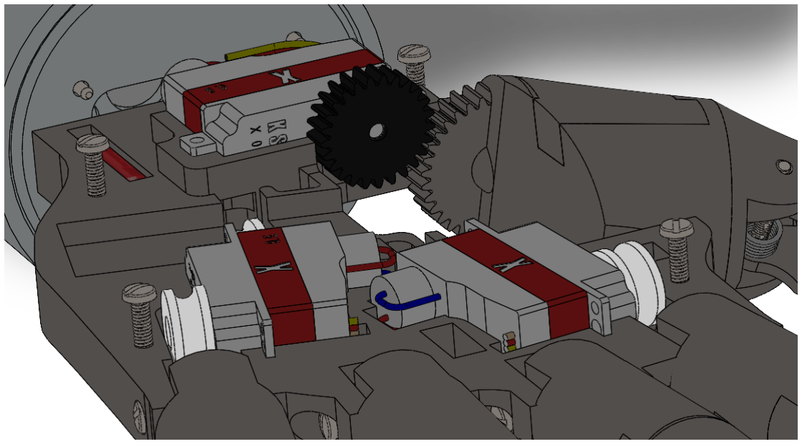
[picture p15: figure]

Figure 22: Thumb abduction gear mounting

### 7.5 Covers and Wrist

***NOTE: Leave dorsal palm covers off—install after hardware & software section

1. After the motors have been wired, electronics soldered, board has been programed and Bluetooth module inserted, proceed with cover and wrist installation.
2. Cut 4 M2X25 screws to an 18mm thread length. Install palmar and dorsal covers ensuring not to pinch any of the wires. Then screw in from the dorsal side to the palmar side (see Figure 23 below).
3. After this you can install the wrist mounts. Make sure the power wires are routed through the wrist and proceed to screw in the R/L-Wrist-HandMount using four of the #4 x 1/2" Flat Head Sheet Metal Screws.
4. Fish the wires through the R/L-Wrist-HandAdapter then mount it to the R/L-Wrist-HandMount with four M3 x 0.5mm bolts.
5. Print rubber grip template found on the next page; use template to cut Neoprene textured adhesive rubber and attach to the palm.

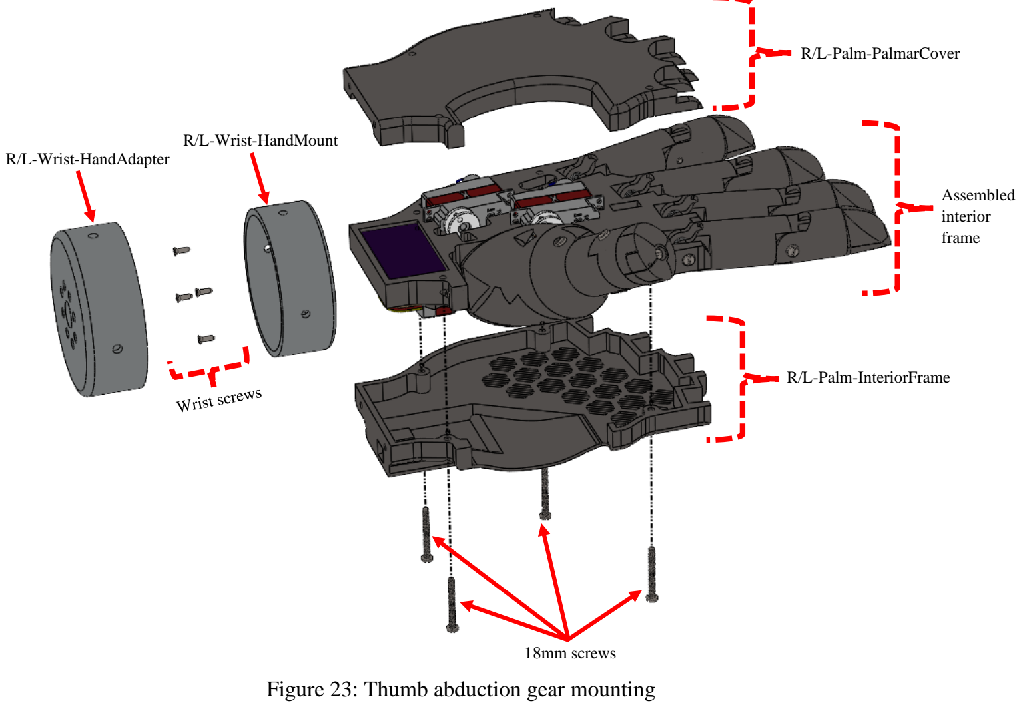
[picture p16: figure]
R/L-Wrist-HandAdapter; R/L-Wrist-HandMount; 18mm screws; R/L-Palm-PalmarCover; R/L-Palm-InteriorFrame; Assembled interior frame

Figure 23: Thumb abduction gear mounting

### Left Hand

### Right Hand

### Drawings are to scale: Print out and use as a template to cut the

textured rubber for the palm grip.

## 8. Hardware and Software

### 8.1 Soldering

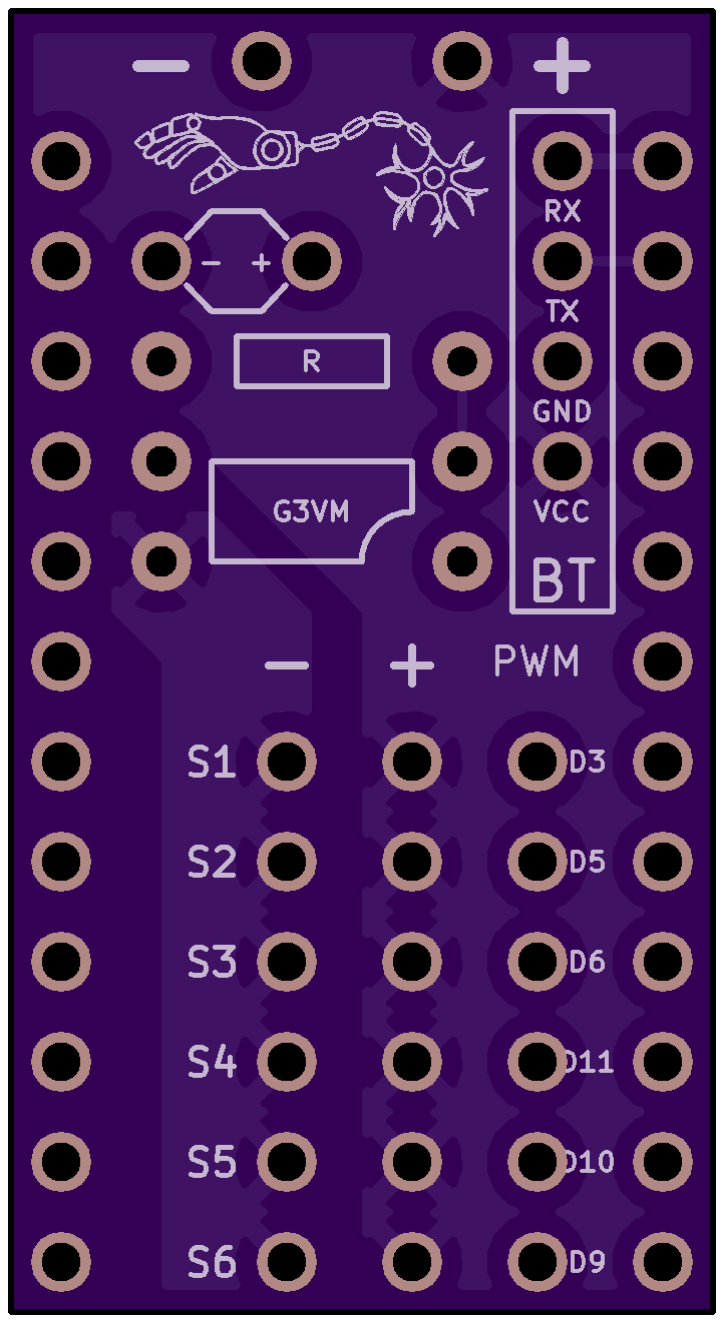
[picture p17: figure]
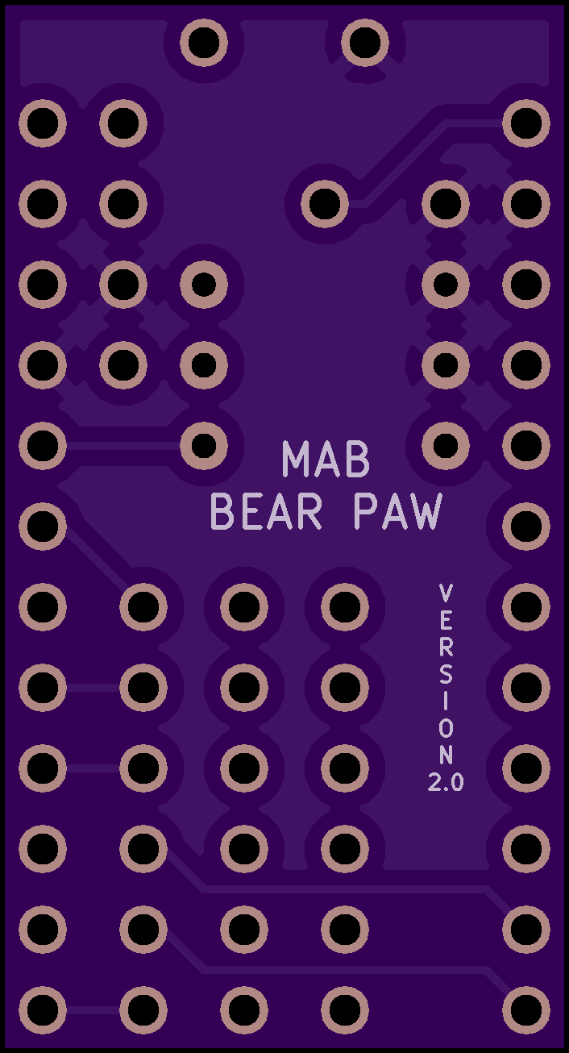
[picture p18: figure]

1. Solder the resistor to the PCB where the R location is (Figure 24a).
2. Solder the relay to the PCB where the G3VM location is, in the orientation of the dot present on the relay itself, aligning it with the cutout on the PCB drawing (Figure 24a).
3. Cut 4 pieces of the power wire about 2-3 feet (or to your desired length) and solder them to the thru-holes shown in Figure 25 below.
4. Connect the other end of these wires separately to the two DC Barrel Jack Adapter – Female parts following the positive and negative wire labeling (these will need to be removed and reinstalled when placing the palm covers on at the end).
Figure 24a: PCB front | Figure 24b: PCB back

5. Solder the other half of the servo wires to the below thru-holes. Brown is negative, red is positive, and yellow is PWM (Figure 26).

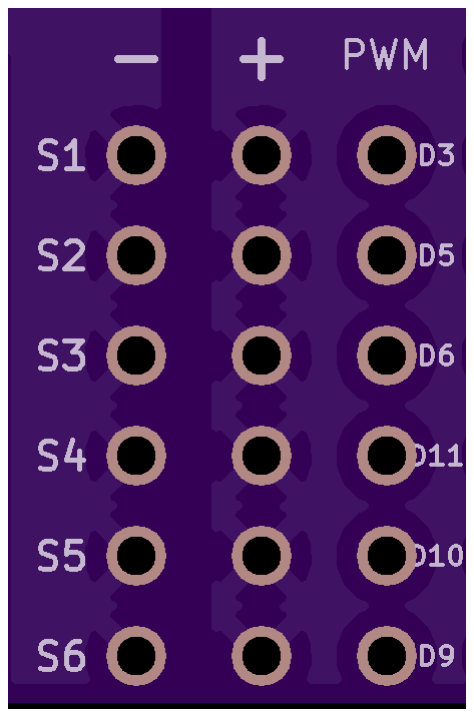
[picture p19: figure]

6. Create a 4 pin female connector as described in Section 7.3.1 (Wire Cutting) with 4 equal length wires of 85 mm. Then solder the end onto the RX, TX, GND and VCC thru-holes as shown in Figure 27 below.

Figure 26: Servo mount thru-holes

Figure 27: Bluetooth mount thru-holes

7. Desolder the Bluetooth header pins and resolder new 90° header pins in the opposite direction (into the board), as this saves space. It is difficult to desolder so buying an extra Bluetooth module may be needed.
8. Clean up any large amounts of solder on the back of the PCB with wire cutters.
9. Solder the header pins to the Arduino ProMini around the outside: two 12-pin headers, and one 6-pin header (see Figure 28a below).
a. For the two 12-pin headers, the pins should be soldered with the short end going into the back face (underside) of the Arduino ProMini, and the longer ends sticking downwards (see Figure 28b below).
b. For the 6-pin headers, the short end should be going into the front face of the Arduino, and the long ends sticking upwards (see Figure 28b below).

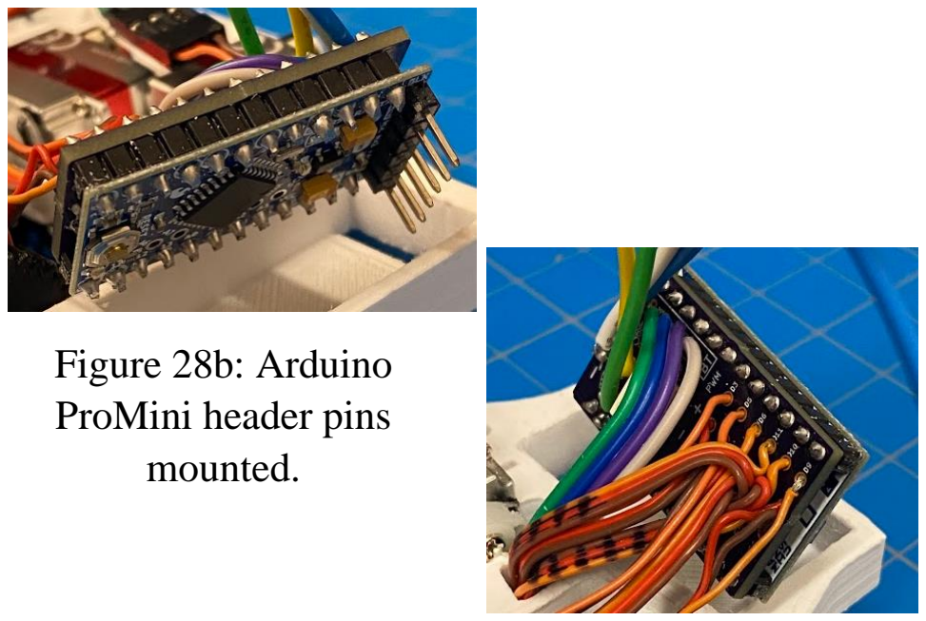
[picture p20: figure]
Figure 28b: Arduino ProMini header pins mounted.

10. Now solder the PCB to the Arduino. The back face of the Arduino should be facing the back face of the PCB (see Figure28b and c). Make sure everything is done because you can’t go back from this step.

### 8.2 Wiring

1. Wires for servos 1, 4 and 5 go through port 1 (Figure 29) of the palm frame, from the dorsal side through to the palmar side. Servo 2 will need to be popped out of its place momentarily while wires are passed through.
2. Wires for the Bluetooth module will go through port 1 (Figure 29) of the palm frame, from the palmar side to the dorsal side where the Bluetooth module is located. Servo 2 will (again) need to be popped out of its place momentarily while wires are passed through.

Figure 28a: Arduino
ProMini header pin location.

Figure 28c: Arduino ProMini and PCB mounted.

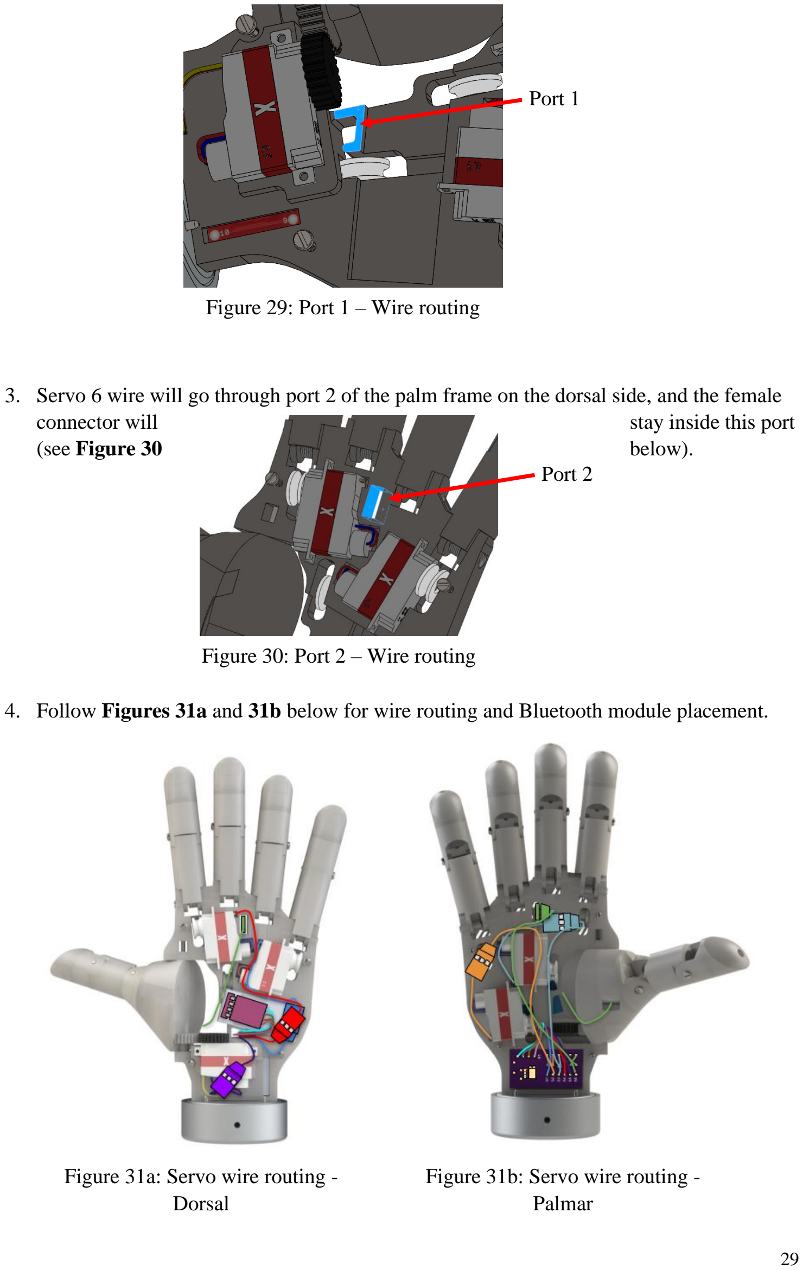
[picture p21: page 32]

3. Servo 6 wire will go through port 2 of the palm frame on the dorsal side, and the female
connector will | stay inside this port
(see Figure 30 | below).
4. Follow Figures 31a and 31b below for wire routing and Bluetooth module placement.

Port 1

Figure 29: Port 1 – Wire routing

Port 2

Figure 30: Port 2 – Wire routing

Figure 31a: Servo wire routing -Dorsal

Figure 31b: Servo wire routing -Palmar

### 8.2 Programming

1. Leave the Bluetooth module unconnected and connect the FTDI cable to program the hand (make sure jumper on the FTDI is on the 3.3V setting).
2. The FTDI board will require that you download the drivers. Link can be found below: https://ftdichip.com/drivers/d2xx-drivers/
The driver version used was the 2.12.28 but this is no longer supported. It can be found at the link above but newer version should still work.
3. Download and install Arduino IDE: https://www.arduino.cc/en/software.
Then make the following board selections: see Figure 32 below.

Board: Arduino Pro or Pro Mini

Processor: ATmega328P(3.3 V, 8 MHz)

4. Download the Arduino script from GitHub and upload to the board.
5. Now download Processing (currently using version 3.5.4) from the following link: https://processing.org/de/download/
Under the Sketch tab, go to Import Library then Add Library. Search and add ControlP5 library by Andreas Schlegel. (http://www.sojamo.de/) See Figure 33 below.

Figure 32: Arduino board and processor settings

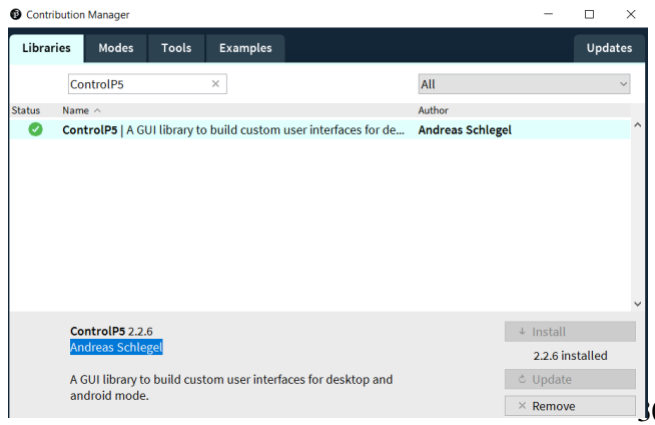
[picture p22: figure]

Figure 33: ControlP5 library installation procedures

6. Now you can plug in the two Wall Adapters into mains power and connect the two DC Barrel Jack Adapter – Female parts to them.
7. Then download the GUIProcessing script from GitHub and run it.
8. Upon first run, the script will likely give an error because the wrong port is selected and the GUI will remain black. The code should have provided a list of the available communication ports in the Console. Cycle through these on line 50 shown below (“COM5”) until the GUI successfully runs.

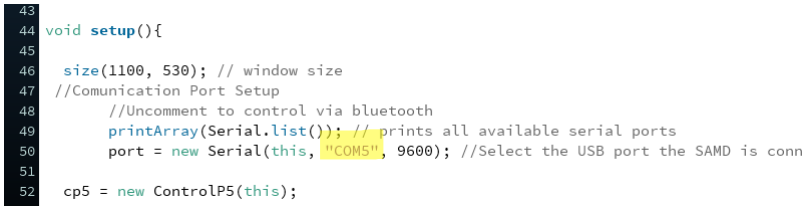
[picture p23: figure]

9. Now you can turn the virtual knobs and press the virtual buttons to make sure everything works. See the GUI Figure 35 below.
a. To go into any grasp, toggle the virtual button (press it twice). To go back to Grasp 1 (i.e., rest), toggle it.

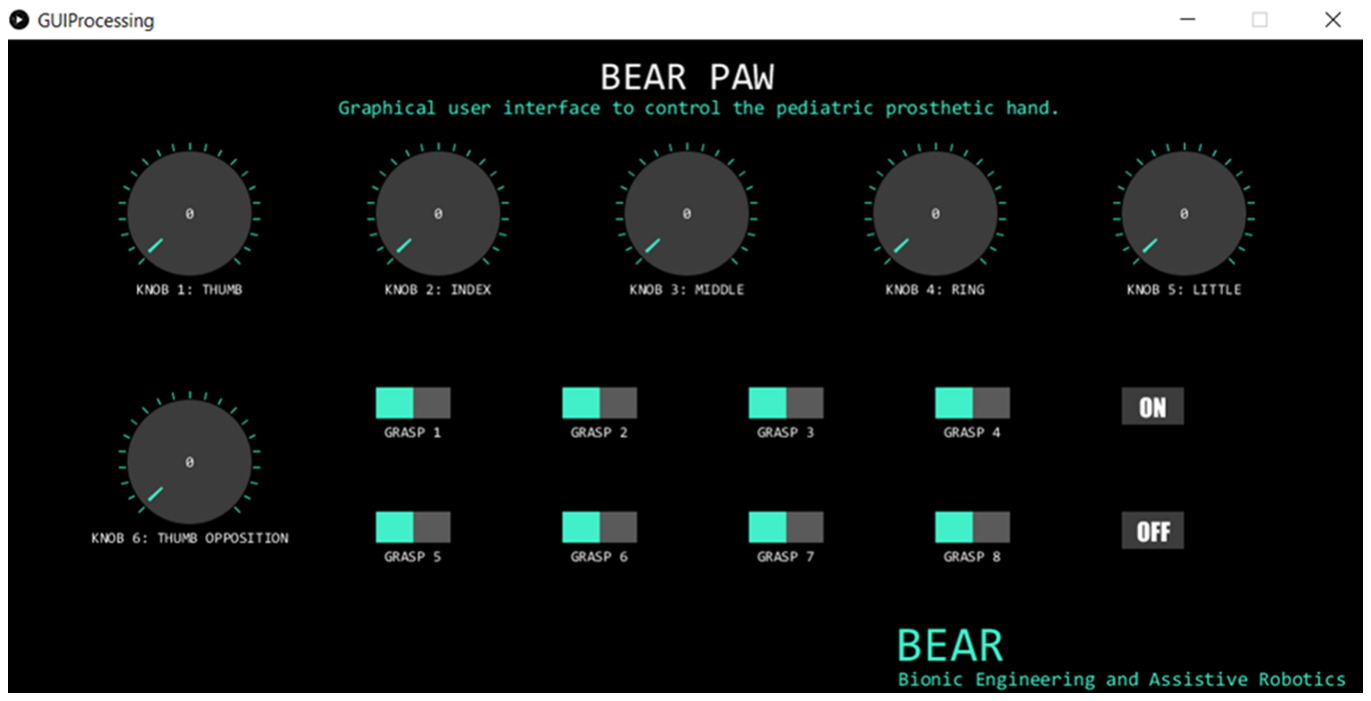
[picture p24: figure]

10. Once you successfully run the GUI in Processing, you can take the FTDI out and plug in the Bluetooth module. You will have to select the Communication port again. Make sure everything works again before you put the palm covers on.

If successful you can now put on the palm covers and wrist mounts.

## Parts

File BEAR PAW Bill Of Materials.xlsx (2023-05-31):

BEAR PAW - Bill of Materials
Date Updated: 7/26/2022
Item | Description | Vendor | Part No. | Link | Qty. | Cost/Item | Ext. Cost | Notes
SENSORS/ELECTRONICS
KST X08N V5.0 | Micro Servo Motor with no mounting flanges | Alofthobbies | X08N | https://alofthobbies.com/kst-x08n.html | 1 | $39.00 | $39.00
KST X08H V5.0 | Micro Servo Motor with top mounting flanges | Alofthobbies | X08H | https://alofthobbies.com/kst-x08h-servo-2-8kg-38-oz-in-09-sec-8-grams-wide-voltage.html | 1 | $39.00 | $39.00
KST X08 V5.0 | Micro Servo Motor with side mounting flanges | Alofthobbies | X08 | https://alofthobbies.com/kst-x08-servo-2-8kg-38-oz-in-09-sec-8-grams.html | 4 | $39.00 | $156.00
Breakout Board | 2 layer electronics breakout board, 17.8 x 33.0mm | OSHPARK | N/A | https://oshpark.com/ | 1 | $4.50 | $4.50 | Comes as 3 boards. After a protoboard is developed, design a PCB. Upload the BEAR_PAW_Gerbers.zip KiCad file folder
Solid State Relay | Omron, Solid State Relay - PCB Mount, 3 A, 60 V | Mouser Electronics | 653-G3VM-61AR1 | https://www.mouser.com/ProductDetail/Omron-Electronics/G3VM-61AR1?qs=wnTfsH77Xs74FCx6Uqk9GQ%3D%3D | 1 | $6.90 | $6.90
Resistor | 5,600 Ohm Resistor, 5%, 0.5W Through Hole Resistor | DigiKey | S5.6KHCT-ND | https://www.digikey.com/en/products/detail/stackpole-electronics-inc/CFM12JT5K60/1741974?s=N4IgTCBcDaIMIDECyBGMApAKgVgNIDYAGEAXQF8g | 1 | $0.10 | $0.10
Arduino Pro Mini 328 - 3.3V/8MHz | Micro Controller | Sparkfun | DEV-11114 | https://www.sparkfun.com/products/11114 | 1 | $9.95 | $9.95
FTDI Mini USB to TTL | HiLetgo FT232RL FTDI Mini USB to TTL Serial Converter Adapter Module 3.3V 5.5V FT232R Breakout FT232RL USB to Serial Mini USB to TTL Adapter Board for Arduino | Amazon | B00IJXZQ7C | https://www.amazon.com/HiLetgo-FT232RL-Converter-Adapter-Breakout/dp/B00IJXZQ7C/ | 1 | $5.99 | $5.99 | Make sure to change the jumper pin to the 3.3V option as this is the voltage for the arduino pro mini
Bluetooth Module | DSD Tech HC-05 Bluetooth Serial Module | Amazon | B01G9KSAF6 | https://www.amazon.com/DSD-TECH-HC-05-Pass-through-Communication/dp/B01G9KSAF6/ | 1 | $9.99 | $9.99
Power Wires | 22 Gauge Silicone wire spool red 25ft and black 25ft Flexible 22 AWG Stranded Copper Wire | Amazon | B07HGT44XY | https://www.amazon.com/BNTECHGO-Silicone-Flexible-Strands-Stranded/dp/B07HGT44XY/?th=1 | 1 | 9.06 | $9.06
Connector Kit | 1004pcs Crimp Connector Kit with 2.54 mm Crimp Pin Connector Housings, Single Row Male Headers, Male/Female Crimp Pins and Ribbon Cable | Amazon | ‎ B078RRPRQZ | https://www.amazon.com/Dupont-Connector-Kit-Connectors-Plusivo/dp/B078RRPRQZ/ | 1 | 12.99 | $12.99
Crimping Tool | Micro Connector Pin Crimping Tool, Yangoutool Micro Ratcheting Crimper 32-20AWG for D-Sub,Open Barrel suits Molex,JST,JAE | Amazon | B087BGTH1Y | https://www.amazon.com/dp/B087BGTH1Y | 1 | 22.99 | $22.99
Wall Adapter | AC/DC Wall Mount Adapter 5V, 20W | DigiKey | 102-4196-ND | https://www.digikey.ca/en/products/detail/cui-inc/SWI25-5-N-P5/7070092 | 2 | $23.92 | $47.84
Wall Jack | DC Barrel Jack Adapter - Female | Sparkfun | 10288 | https://www.sparkfun.com/products/10288 | 2 | $2.95 | $5.90
CENTAURUS Servo Tester STV2.3 | Steering Gear Rudder Detector Spare Parts for RC Aircraft Micro FPV DC 4.8V-6V | Amazon | B09LXTW19G | https://www.amazon.com/CENTAURUS-Steering-Detector-Aircraft-4-8V-6V/dp/B09LXTW19G | 1 | $3.50 | $3.50 | This is only used for testing and is not entirely nesesary.
HARDWARE/MISCELLANEOUS
Bearings - 2mm Bore ID, 5mm OD, 2.5mm Width Double Shielded Miniature Chrome Steel Ball Bearing for Fidget Spinners, Micro Motor, Office Equipment (10 Pack) | Bearing 2 mm ID 5 mm OD | Amazon | B07X9T5F81 | https://www.amazon.com/Donepart-MR52ZZ-Bearings-Miniature-Equipment/dp/B07X9T5F81 | 1 | $9.99 | $9.99
Pulley for KST X08 Servo | Pulley for KST Servo Pack of 4 | Hyperflight | X08-PULLEY | https://www.hyperflight.co.uk/products.asp?code=X08-PULLEY&name=pulley-for-kst-x08-servos-4 | 2 | $12.50 | $25.00
Rotary Shaft 316 Stainless Steel, 2 mm Diameter, 200 mm Long | 2 mm Shaft 200 mm long | McMaster Carr | 1265K17 | https://www.mcmaster.com/1265K17/ | 1 | $12.40 | $12.40
Torsion Spring | Torsion Spring 180 Dregree Right-Hand Wound, 0.186'' OD, Music-Wire Steel, Pack of 6 | McMaster Carr | 9271K665 | https://www.mcmaster.com/9271K665/ | 2 | $5.01 | $10.02
Strength Black Synthetic Cable (5 meters) | Synthetic Cable measures only 0.75mm (0.03") in diameter, 5 meters long,holds up to 45kg | ServoCity | 2908-0075-0005 | https://www.servocity.com/synthetic-cable-black-0-75mm-diameter-5m-length/ | 1 | $2.99 | $2.99
18-8 Stainless Steel Screw | 18-8 Stainless Steel Narrow Cheese Head Slotted Screws M2 x 0.4mm Thread, 25mm Long | McMaster Carr | 91800A023 | https://www.mcmaster.com/91800A023/ | 1 | $10.15 | $10.15
625pcs Heat Shrink Tubing Kit | Heat Shrink Tubing | Amazon | B07QM8249H | https://www.amazon.com/625pcs-Shrink-Tubing-Tubes-Ratio/dp/B07QM8249H/ | 1 | $8.98 | $8.98
Textured Rubber | Multipurpose Neoprene with Crisscross Texture Adhesive-Back Sheet, 12" x 12", 1/32" Thick | McMaster Carr | 8445K61 | https://www.mcmaster.com/8445K61/ | 1 | $16.67 | $16.67
MATERIALS
Smooth-On Dragon Skin | Smooth-On Dragon Skin 10 NV, 2 Pint Set (Moldable material for fingertips) | Douglas & Sturgess Ingredients for Art | MC-1244 | Douglas and Sturgess: Smooth-On Dragon Skin 10 Medium, 2 Pint Set (http://www.douglasandsturgess.com/mm5/merchant.mvc?Screen=PROD&Store_Code=DAS&Product_Code=MC-1244&Category_Code=) | 1 | $32.25 | $32.25
Gorilla Super Glue Gel XL, 25 gram, Clear | Super Glue | Amazon | B082XGL21J | https://www.amazon.com/Gorilla-Super-Glue-transparente-102433/dp/B082XGL21J/ | 1 | $7.99 | $7.99
 |  |  |  |  |  | Total | $510.15

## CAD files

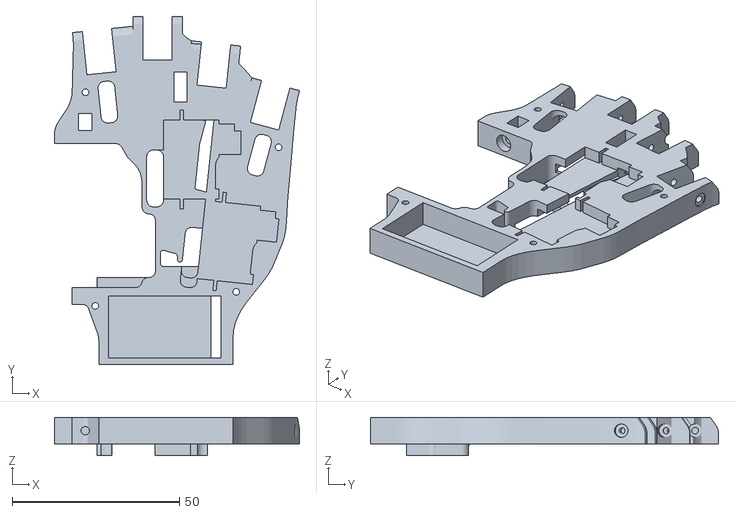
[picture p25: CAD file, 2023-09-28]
Hardware/Left Hand/Palm/L-Palm-InteriorFrame.stl
73.3 x 104.0 x 11.5

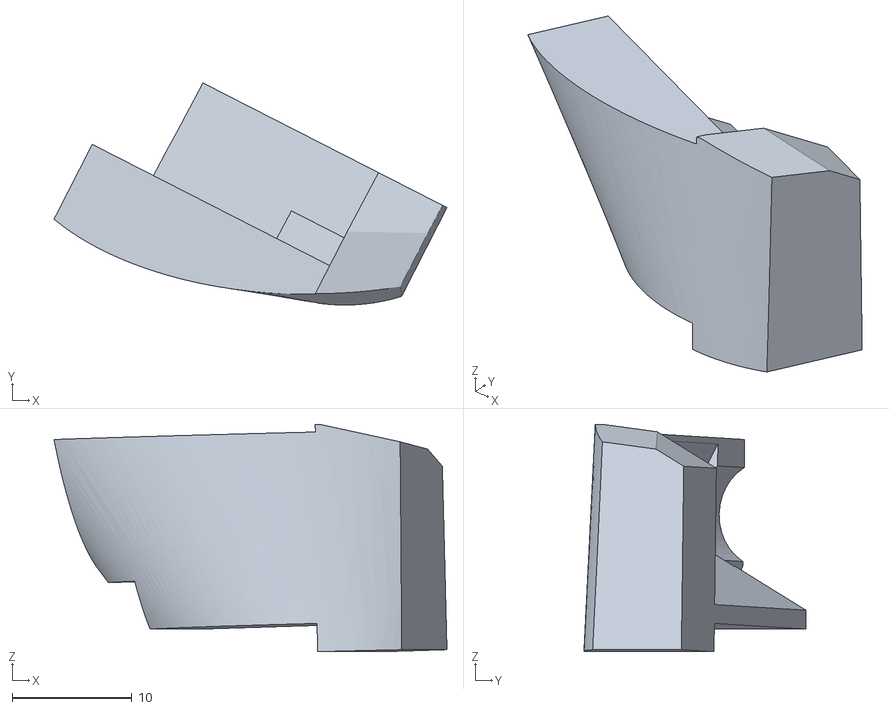
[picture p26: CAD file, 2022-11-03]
Hardware/Left Hand/Thumb/L-D1-PPhal-PPart-PalmDoor.STL
32.8 x 18.6 x 19.0

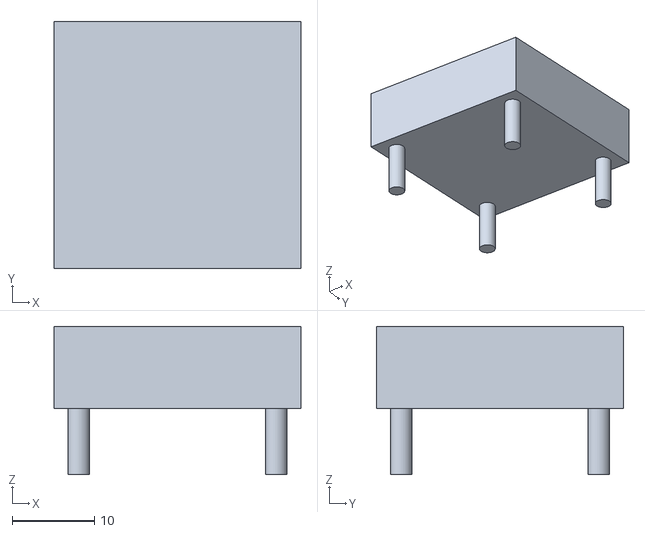
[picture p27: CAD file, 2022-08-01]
Hardware/Right Hand/Finger/R-D2to5-FTNeg2.STL
30.0 x 30.0 x 18.0

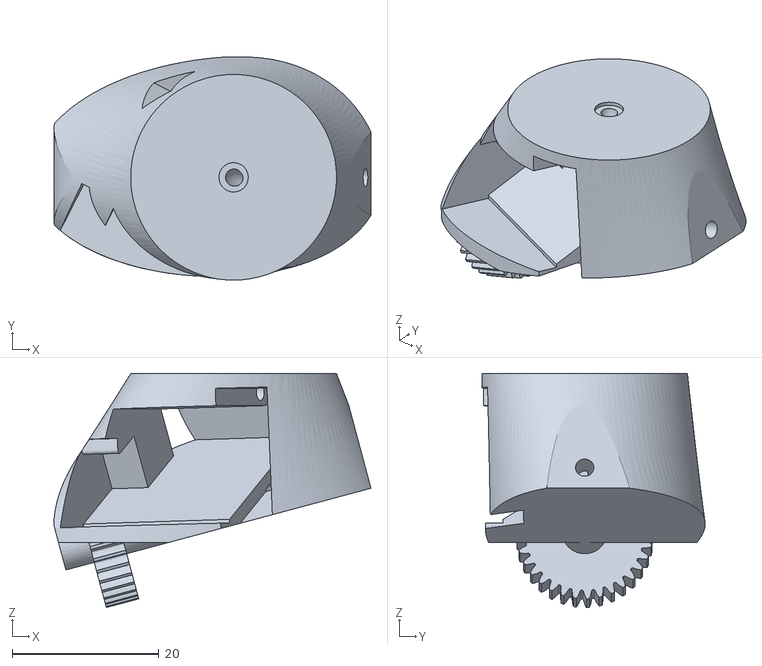
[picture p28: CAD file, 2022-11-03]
Hardware/Right Hand/Thumb/R-D1-PPhal-PPart-PalmGear.STL
43.1 x 30.4 x 31.9

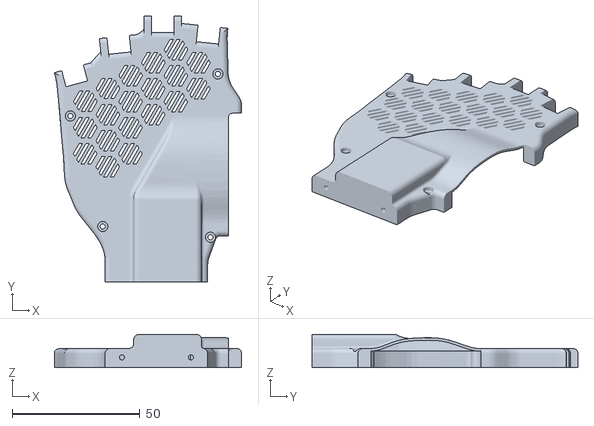
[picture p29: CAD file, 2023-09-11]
Hardware/Left Hand/Palm/L-Palm-DorsalCover.stl
73.3 x 104.0 x 13.0

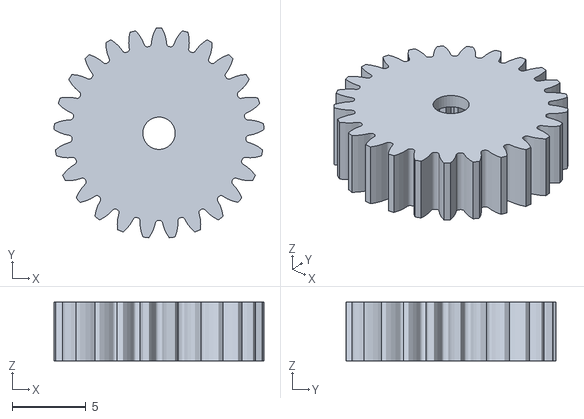
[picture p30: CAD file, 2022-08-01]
Hardware/Left Hand/Thumb/L-D1-PalmGearWheel.STL
14.3 x 14.3 x 4.00

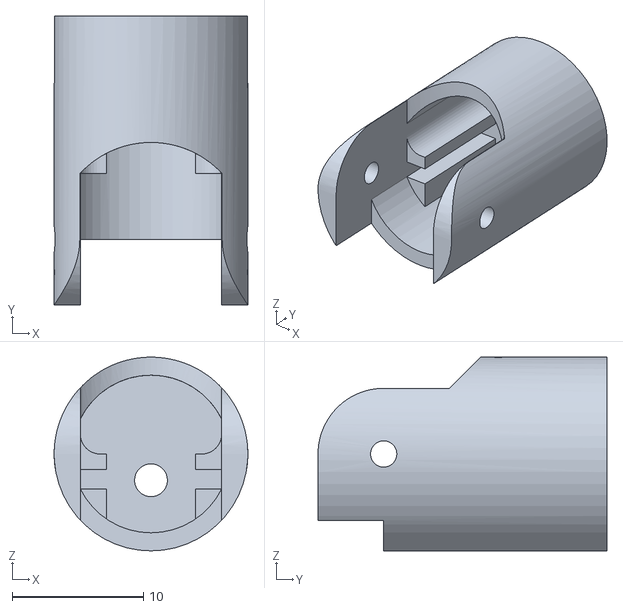
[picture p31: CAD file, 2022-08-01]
Hardware/Right Hand/Finger/R-D2to5-IPhal.STL
14.8 x 22.0 x 14.8

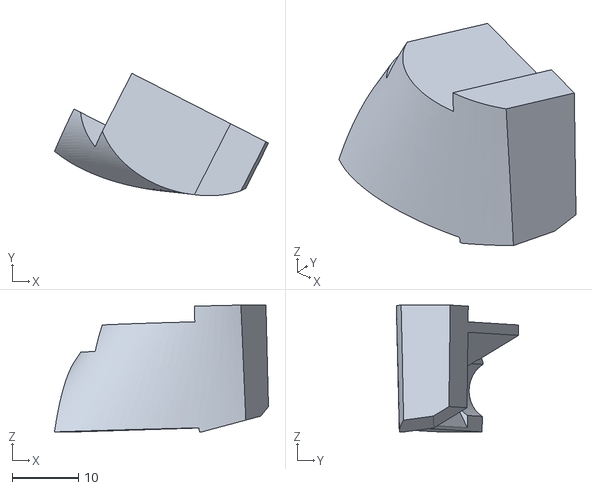
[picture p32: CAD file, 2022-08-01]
Hardware/Right Hand/Thumb/R-D1-PPhal-PPart-PalmDoor.STL
32.3 x 18.5 x 19.2

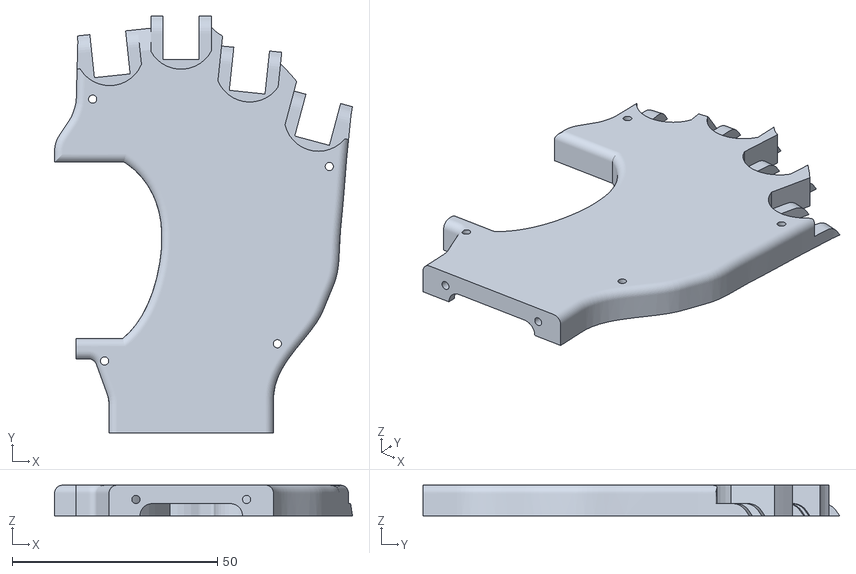
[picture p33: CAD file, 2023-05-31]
Hardware/Left Hand/Palm/L-Palm-PalmarCover.stl
72.6 x 101.5 x 7.50

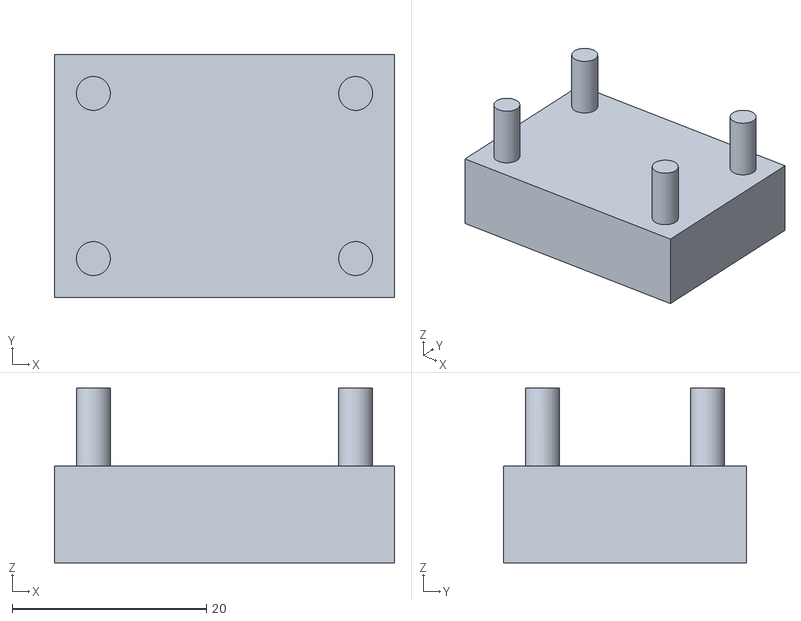
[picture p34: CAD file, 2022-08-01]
Hardware/Left Hand/Thumb/L-D1-FTNeg2.STL
35.0 x 25.0 x 18.0

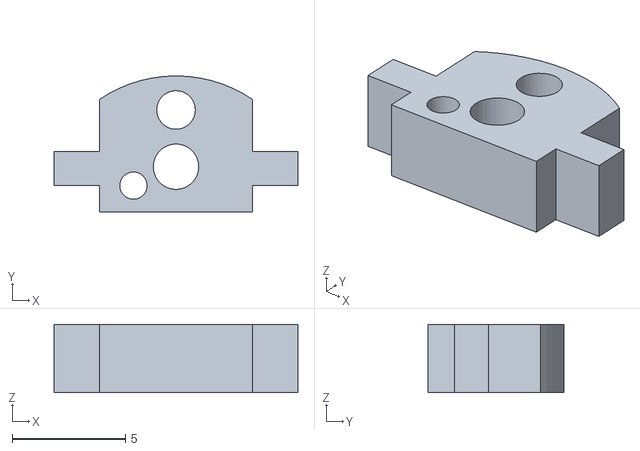
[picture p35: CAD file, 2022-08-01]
Hardware/Right Hand/Finger/R-D2to5-Tensioner.STL
10.8 x 6.00 x 3.00

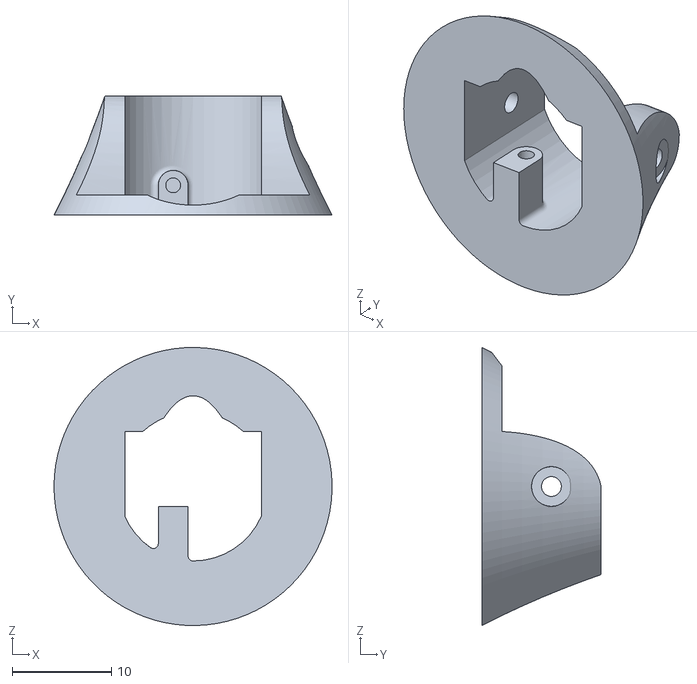
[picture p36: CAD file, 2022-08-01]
Hardware/Left Hand/Thumb/L-D1-PPhal-DPart.STL
28.0 x 12.0 x 28.0

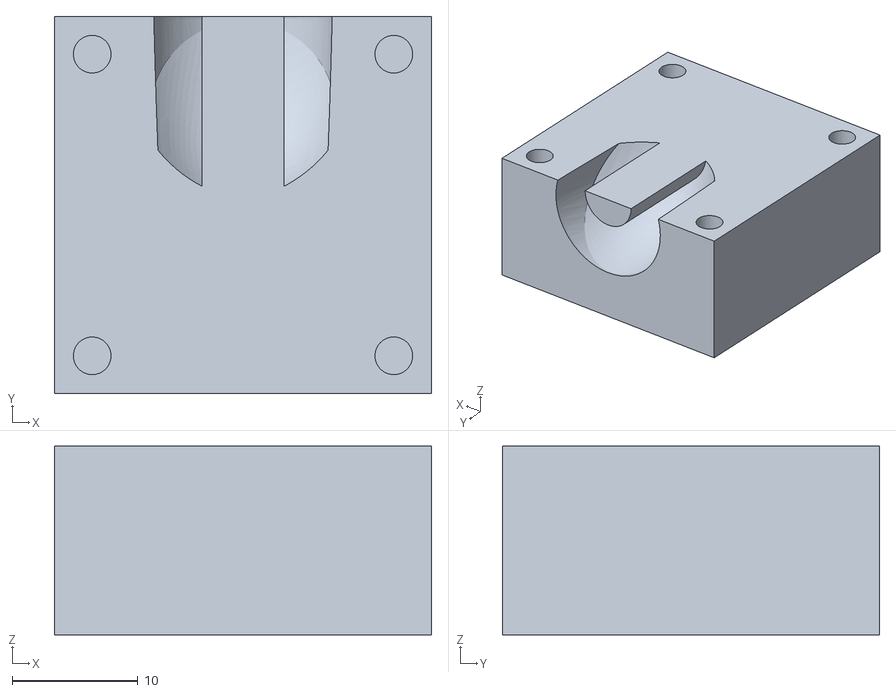
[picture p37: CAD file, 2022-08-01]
Hardware/Right Hand/Finger/R-D2to5-FTNeg1.STL
30.0 x 30.0 x 15.0

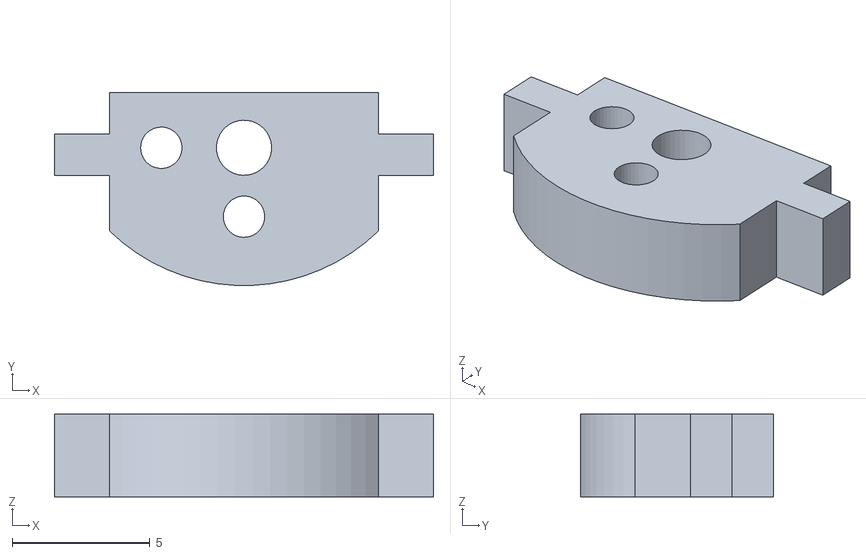
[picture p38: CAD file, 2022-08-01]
Hardware/Left Hand/Thumb/L-D1-Tensioner.STL
13.8 x 6.99 x 3.00

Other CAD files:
Hardware/Right Hand/Palm/R-Palm-InteriorFrame.STL
Hardware/Right Hand/Palm/R-Palm-DorsalCover.STL
Hardware/Right Hand/Palm/R-Palm-PalmarCover.stl
Hardware/Right Hand/Finger/R-D2to5-PPhal-PPart.STL
Hardware/Left Hand/Thumb/L-D1-DPhal-DPart.STL
Hardware/Left Hand/Thumb/L-D1-DPhal-PPart.STL
Hardware/Left Hand/Thumb/L-D1-FTNeg1.STL
Hardware/Left Hand/Thumb/L-D1-IPhal-DPart.STL
Hardware/Left Hand/Thumb/L-D1-IPhal-PPart.STL
Hardware/Left Hand/Thumb/L-D1-PPhal-PPart-PalmGear.STL
Hardware/Right Hand/Finger/R-D2to5-DPhal.STL
Hardware/Right Hand/Finger/R-D2to5-PPhal-DPart.STL

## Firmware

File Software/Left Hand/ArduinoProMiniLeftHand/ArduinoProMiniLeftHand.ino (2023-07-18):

/*Pediatric Prosthetic Hand Control 
 * Left Hand Control
 * Author: Marcus A. Battraw
 * Date: 09-02-2020
 * Arduino Pro Mini (8MHz / 3.3V)
 * Pin Layout Schematic
 * |----FTDI-Header----|
 * |GND GND VCC RX1 TX0|
 * |TX0             RAW|
 * |RX1 Arduino Pro GND|
 * |RST     Mini    RST|
 * |GND             VCC|
 * |D2              A3 |
 * |D3              A2 |
 * |D4              A1 |
 * |D5              A0 |
 * |D6              D13|
 * |D7              D12|
 * |D8    Reset     D11|
 * |D9    Button    D10|
 * |-------------------|
 */
 /* The software of the BEAR PAW is released under the GNU General Public License v3. */
 
#include <Servo.h>
#include <SoftwareSerial.h>

//Define servo object to control each of the servos
Servo servo_6;
Servo servo_5;
Servo servo_4;
Servo servo_3;
Servo servo_2;
Servo servo_1;

//LED for testing
int LED = 13; //LED on pin 13

//PWM Pin Assigenment
int PWM_1 = 9;  //Thumb: S6
int PWM_2 = 10; //Thumb Opposition: s5
int PWM_3 = 11; //Index: S4
int PWM_4 = 6;  //Middle: S3
int PWM_5 = 5;  //Ring: S2
int PWM_6 = 3;  //Little: S1

//On-Off Control
int D2 = 2; //Solid State Relay Control

//Individual Motion ID Numbers
int M_1 = 253; //Thumb
int M_2 = 252; //Thumb Opposition
int M_3 = 251; //Index
int M_4 = 250; //Middle
int M_5 = 249; //Ring
int M_6 = 248; //Little

//Grasp Motion ID Numbers
int G_1  = 247; //Grasp 1
int G_2  = 246; //Grasp 2
int G_3  = 245; //Grasp 3
int G_4  = 244; //Grasp 4
int G_5  = 243; //Grasp 5
int G_6  = 242; //Grasp 6
int G_7  = 241; //Grasp 7
int G_8  = 240; //Grasp 8
int G_9  = 239; //Grasp 9
int G_10 = 238; //Grasp 10
int D_1  = 237; //Demo  1
 
void setup() 
{
  pinMode(LED, OUTPUT);   //Set LED (pin 13) as an Output
  digitalWrite(LED, LOW); //Set LED to start off LOW

  pinMode(D2, OUTPUT);   //Set Solid State Relay (pin D2) as an Output
  digitalWrite(D2, LOW); //Set D2 to start off LOW
  
//Setup the servo PWM (SIG) wire attachement corresponding to the board pins
  servo_6.attach(PWM_1, 1000, 2000); //(pin, min, max) min,max of servo 1000, 2000 us, from data sheet
  servo_6.write(0); //180               //set each position to zero position upon turning on (this motor is fliped)
  servo_5.attach(PWM_2, 1000, 2000);
  servo_5.write(180); // 0
  servo_4.attach(PWM_3, 1000, 2000);
  servo_4.write(180); //0               //This motor is fliped
  servo_3.attach(PWM_4, 1000, 2000);
  servo_3.write(0);  //180              //This motor is fliped
  servo_2.attach(PWM_5, 1000, 2000);
  servo_2.write(0); //180               //This motor is fliped
  servo_1.attach(PWM_6, 1000, 2000);
  servo_1.write(0); // 180                //This motor is fliped
  
  Serial.begin(9600);

}

void loop() 
{
if(Serial.available()> 0){            //Check if their is data available to read
  
  digitalWrite(D2, HIGH);             //Close the Solid State Relay to allow for motor movement

  unsigned char val = Serial.read();  //Read the data
  
  //Blue LED On
  if(val == 255){                     //Check first Char
        digitalWrite(LED, HIGH);      //LED on, for testing and debuging the circuit
  }

  //Blue LED Off
  if(val == 254){ 
        digitalWrite(LED, LOW);        //LED off
  }

//Servo Knob Control
//Servo 1: Thumb
  if(val == M_1){
    delay(15);
    unsigned char val = Serial.read();
      if(val<= 180){
       servo_6.write(val);
    }
  }

//Servo 2: Thumb Opposition
 if(val == M_2){
   delay(15);
   unsigned char val = Serial.read();
     if(val<= 180){
      int m = map(val, 0, 180, 180, 0);
      servo_5.write(m);
    }
  }

//Servo 3: Index
  if(val == M_3){
    delay(15);
    unsigned char val = Serial.read();
      if(val<= 180){
       int m = map(val, 0, 180, 180, 0);
       servo_4.write(m);
    }
  }

//Servo 4: Middle
  if(val == M_4){
    delay(15);
    unsigned char val = Serial.read();
      if(val<= 180){
       servo_3.write(val);
    }
  }

//Servo 5: Ring
  if(val == M_5){
    delay(15);
    unsigned char val = Serial.read();
      if(val<= 180){
       servo_2.write(val);
    }
  }

//Servo 6: Little
  if(val == M_6){
    delay(15);
    unsigned char val = Serial.read();
      if(val<= 180){
       servo_1.write(val);
    }
  }    

//Grasp Control

//Grasp 1: Resting Position // Platfrom 
if(val == G_1){
  //Define the value for each servo to preform the specified grasp
  int val_1 = 0; //Thumb
  int val_2 = 180;   //Thumb Opposition
  int val_3 = 180;   //Index
  int val_4 = 0; //Middle
  int val_5 = 0; //Ring
  int val_6 = 0; //Little
  //Write the values to each servo
  servo_6.write(val_1);
  servo_5.write(val_2);
  servo_4.write(val_3);
  servo_3.write(val_4);
  servo_2.write(val_5);
  servo_1.write(val_6);
  }    

//Grasp 2: Medium Wrap // Cylindrical Grip
if(val == G_2){ // This is the same thing, it's redundant
  int val_1 = 150;  //Thumb //int val_1 = 110;  //Thumb
  int val_2 = 0;  //Thumb Opposition
  int val_3 = 0; //Index
  int val_4 = 180;   //Middle
  int val_5 = 180;   //Ring
  int val_6 = 180;   //Little

  servo_5.write(val_2);
  delay(1000);
  servo_4.write(val_3);
  servo_3.write(val_4);
  servo_2.write(val_5);
  servo_1.write(val_6);
  delay(10);
  servo_6.write(val_1);

  }  

  //Grasp 3: Lateral Pinch
if(val == G_3){
  int val_1 = 180;  //Thumb
  int val_2 = 50; //Thumb Opposition
  int val_3 = 0; //Index
  int val_4 = 180;   //Middle
  int val_5 = 180;   //Ring
  int val_6 = 180;   //Little
 
  servo_4.write(val_3);
  servo_3.write(val_4);
  servo_2.write(val_5);
  servo_1.write(val_6);
  delay(1000);
  servo_5.write(val_2);
  delay(1000);
  servo_6.write(val_1);

  }  

//Grasp 4: Spherical Grip
if(val == G_4){ // This is the same thing, it's redundant
  int val_1 = 110;  //Thumb //int val_1 = 110;  //Thumb
  int val_2 = 0;  //Thumb Opposition
  int val_3 = 50; //Index
  int val_4 = 130;   //Middle
  int val_5 = 110;   //Ring
  int val_6 = 110;   //Little

  servo_5.write(val_2);
  delay(1000);
  servo_4.write(val_3);
  servo_3.write(val_4);
  servo_2.write(val_5);
  servo_1.write(val_6);
  delay(10);
  servo_6.write(val_1);

  }  
  
  //Grasp 5 : Tripod
if(val == G_5){
  int val_1 = 150; //Thumb
  int val_2 = 50; //Thumb Opposition
  int val_3 = 30;  //Index
  int val_4 = 180;  //Middle
  int val_5 = 180;   //Ring
  int val_6 = 180;   //Little
  
  servo_3.write(val_4);
  servo_2.write(val_5);
  servo_1.write(val_6);
  delay(1000);
  servo_6.write(val_1);
  servo_5.write(val_2);
  servo_4.write(val_3);
  }  

  //Grasp 6: Hook
if(val == G_6){
  int val_1 = 150;  //Thumb
  int val_2 = 0;  //Thumb Opposition
  int val_3 = 0; //Index
  int val_4 = 180;   //Middle
  int val_5 = 180;   //Ring
  int val_6 = 180;   //Little

  servo_4.write(val_3);
  servo_3.write(val_4);
  servo_2.write(val_5);
  servo_1.write(val_6);
  delay(1000);
  servo_5.write(val_2);
  delay(1000);
  servo_6.write(val_1);

  } 
    
  //Grasp 7: Extension Grip
if(val == G_7){
  int val_1 = 50;  //Thumb
  int val_2 = 0;  //Thumb Opposition
  int val_3 = 150; //Index   // 30 deg
  int val_4 = 50;   //Middle // 30 deg
  int val_5 = 30;   //Ring   // 30 deg
  int val_6 = 30;   //Little // 30 deg

  servo_5.write(val_2);
  delay(1000);
  servo_4.write(val_3);
  servo_3.write(val_4);
  servo_2.write(val_5);
  servo_1.write(val_6);
  delay(10);
  servo_6.write(val_1);

  } 

  //Grasp 8: Diagonal Volar Grip // Not the correct grip
if(val == G_8){
  int val_1 = 160;  //Thumb //int val_1 = 110;  //Thumb
  int val_2 = 0;  //Thumb Opposition
  int val_3 = 0; //Index
  int val_4 = 180;   //Middle
  int val_5 = 180;   //Ring
  int val_6 = 180;   //Little

  servo_4.write(val_3);
  servo_3.write(val_4);
  servo_2.write(val_5);
  servo_1.write(val_6);
  servo_5.write(val_2);
  delay(1000);
  servo_6.write(val_1);
  } 

  //Grasp 9: Pulp Pinch
if(val == G_9){
  //Define the value for each servo to preform the specified grasp
  int val_1 = 160; //Thumb
  int val_2 = 20;   //Thumb Opposition
  int val_3 = 0;   //Index
  int val_4 = 0; //Middle
  int val_5 = 0; //Ring
  int val_6 = 0; //Little
  //Write the values to each servo
    
  servo_5.write(val_2);
  delay(1000);
  servo_6.write(val_1);
  //delay(1000);
  servo_4.write(val_3);
  servo_3.write(val_4);
  servo_2.write(val_5);
  servo_1.write(val_6);
  } 

    
  //Grasp 10: Point
if(val == G_10){
  int val_1 = 120;   //Thumb
  int val_2 = 0; //Thumb Opposition
  int val_3 = 180;   //Index
  int val_4 = 180;   //Middle
  int val_5 = 180;   //Ring
  int val_6 = 180;   //Little
  
  servo_6.write(val_1);
  servo_5.write(val_2);
  servo_4.write(val_3);
  servo_3.write(val_4);
  servo_2.write(val_5);
  servo_1.write(val_6);
  }  


  //Demo
if(val == D_1){
    servo_1.write(90);
    delay(100);
    servo_2.write(90);
    delay(100);
    servo_1.write(0);
    servo_3.write(90);
    delay(100);
    servo_2.write(0);
    servo_4.write(90);
    delay(150);
    servo_3.write(0);
    servo_1.write(90);//added
    delay(50);
    servo_4.write(180);
    delay(50);        //added
    servo_2.write(90);//added
    delay(100);
    servo_1.write(0);
    servo_3.write(90);
    delay(100);
    servo_2.write(0);
    servo_4.write(90);
    delay(150);
    servo_3.write(0);
    servo_1.write(90);//added
    delay(50);
    servo_4.write(180);
    delay(50);        //added
    servo_2.write(90);//added
    delay(100);
    servo_1.write(0);
    servo_3.write(90);
    delay(100);
    servo_2.write(0);
    servo_4.write(90);
    delay(150);
    servo_3.write(0);
    servo_1.write(90);//added
    delay(50);
    servo_4.write(180);
    delay(50);        //added
    servo_2.write(90);//added
    delay(100);
    servo_1.write(0);
    servo_3.write(90);
    delay(100);
    servo_2.write(0);
    servo_4.write(90);
    delay(150);
    servo_3.write(0);
    delay(50);
    servo_4.write(180);
  }  


 
 }

}

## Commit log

2022-08-01 Create Bill of Materials
2023-07-18 Create ArduinoProMiniRightHand
2023-07-18 Create ArduinoProMiniRightHand\Read me
